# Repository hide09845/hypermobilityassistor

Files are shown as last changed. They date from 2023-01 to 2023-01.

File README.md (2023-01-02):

# The HAND
The HAND (A.K.A. the Hypermobility Assistance Device) is a combination wrist and knuckle brace that intends to provide a free, open-source, and 3d-printable alternative to the pricey and/or usually under/overeffective wrist braces on the market.

# What is the HAND made up of?
The HAND is composed of four primary parts- the upper plate, the lower plate, the upper cuff, and the lower cuff. 

![An image of the HAND Four white arrows are pointing towards the upper plate, lower plate, upper cuff, and lower cuff. The upper plate is the largest of the four parts, appearing as a thin piece that spans a little bit over the knuckle, and connects to the upper cuff via a screw located on the wrist joint, allowing it to rotate in tandem with the wrist. The upper cuff is a semicylinder, with two rectangular "wings" that allow it to connect to the upper plate. The lower cuff is identical to the upper cuff, but with a circle taken out of the area near the wrist joint to allow it to move. The lower cuff is attached to the upper cuff via six rubber bands, with only 3 visible in the image. The lower plate is not directly touching the upper plate, but is connected with four elastic cords, the ends of which have cord stops to allow for adjustable tightness.](https://mayamainvert.neocities.org/hand2.jpg)

They will be referred to as such for the remainder of this document.

# What does it excel at?
The HAND mechanically limits the rotation of your wrist vertically and horizontally, meaning your wrist's mobility will approximately match that of the average person. This is built for fine motor activities such as writing or drawing, as well as any activity that requires a large amount of wrist movement. This offloads much of the muscular usage required to keep your joints from overextending to the device, reducing the pain and fatigue caused by repetitive activities. 

The HAND **will** help reduce pain from typing. However, it limits horizontal movement of the wrist to the wiggle room of the device (and the lower plate may interact with the keyboard unless you are typing with your hands raised), which can make typing awkward in some positions.

# Warnings
Do not eat while wearing the HAND. Like most other 3d-printed goods, pieces of food and dirt can get stuck in the grooves of the print. The HAND may alleviate pain while eating with silverware, but it will pose an actual danger to your health. 

Do not lick the HAND or place your mouth on it. Again, dirt and bacteria WILL get stuck in the grooves of the print, and you WILL be at risk of illness.

# How to scale the HAND in your software
Note: The upper plate, upper cuff, and lower cuff MUST be scaled with each other without any stretching. The lower plate can be whatever size fits your palm, as long as the cord/string/wire you use to connect it to the upper plate fits both sets of holes. 

What you need (aside from the main pieces)

- Two screws and two nuts, the size is determined by how much/whether you scaled the device. Measure the hole attached to the wings of the upper cuff to figure out the screw and nut size.
- A sheet of padding of a thickness that you decide
- Cord/string/wire of your choice, preferably elastic, and four cord stops for adjustability
- Six rubber bands of a reasonable size (they can be double wrapped to shorten them)

Measure your hand from the base of the metacarpus to the edge of your knuckle, then scale the upper plate such that the place that the plate cuts off (not including the "wings" of the plate) extends about 1.5 to 2.5cm past your knuckle. 

this

Don't worry too much, as long as it braces your knuckle joint. If it's correctly calibrated, your knuckle shouldn't be able to hyperextend more than 15+-5 degrees without extensive effort.

Place the wings of the upper plate through the wings of the upper cuff so the holes match, then slot the two screws in outwards (such that if you screwed the nuts on, they would face outward). Then, screw the nuts on. 

After this, cut your cord into two long pieces. You can trim it down later, or just leave it long. Slot the cord through the holes in the lower plate (two holes per cord). Pretty much any configuration would work, but I have it slotted through like so:

Image of the lower hand plate, the cord is slotted outwardly on each side

After this, you're going to want to place one end of the cord into each hole of the upper plate, then attach your cord stops.

so2

Then, double wrap the 6 rubber bands and place them onto the little sets of protruding bits on the upper and lower cuff such that it would hold the cuff together. You're gonna want to put your wrist in now to see what thickness of padding you'll need.

Finally, you will want to attach your padding to the upper and lower cuff. You can cut it out and just superglue or hot glue it, but make sure that it fits first by putting it in unadhered, maybe wear it around a bit. If it falls out, it's too loose, if it crushes your wrist/cuts off bloodflow at all you may want to get a different thickness of padding. This is what mine looks like:

This is what mine looks like

# Disclaimers

- The HAND is built for the right hand. You will need to mirror it for usage on the left hand.
- The HAND was designed by a team of two, including myself. I only take partial credit for the design.
- The HAND is a prototype that was designed around my wrist and hand. It may not fit perfectly on all bodies. 
- Do not wear the HAND if you are experiencing any pain as a result of wearing it. 
- If the HAND results in any injury, contact me (mayamainvert@proton.me) so I can place a disclaimer and/or update the STL, or make a pull request. If it cuts the skin, disinfect the wound then file/sand down the area that resulted in a cut. It shouldn't be able to cut you, but some people have more sensitive skin than me and I don't exactly have a broad sample set.
- Contact me (mayamainvert@proton.me) if anything is unclear.

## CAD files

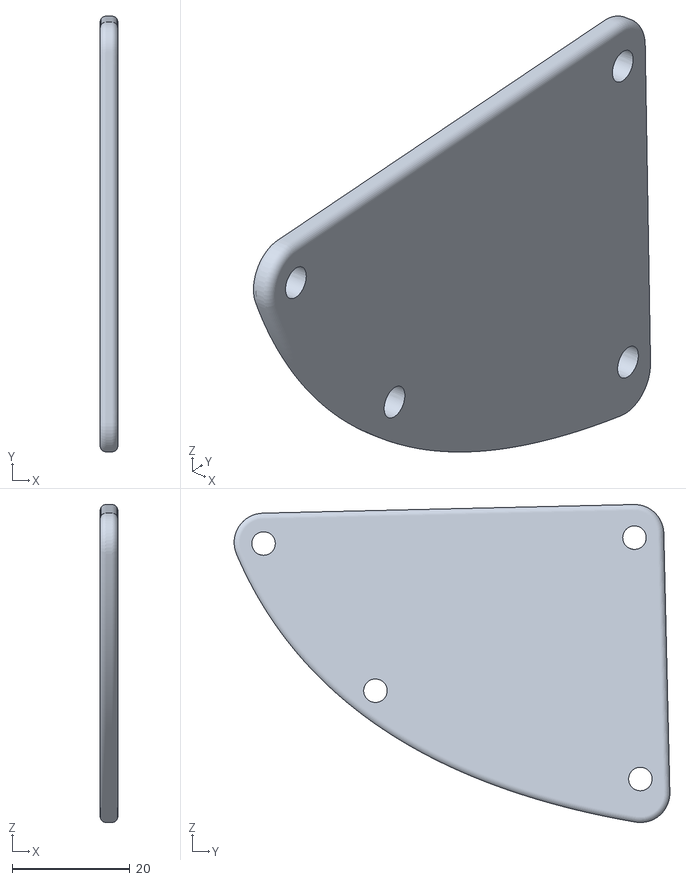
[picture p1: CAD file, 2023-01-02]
lower plate.stl
3.00 x 74.0 x 54.0

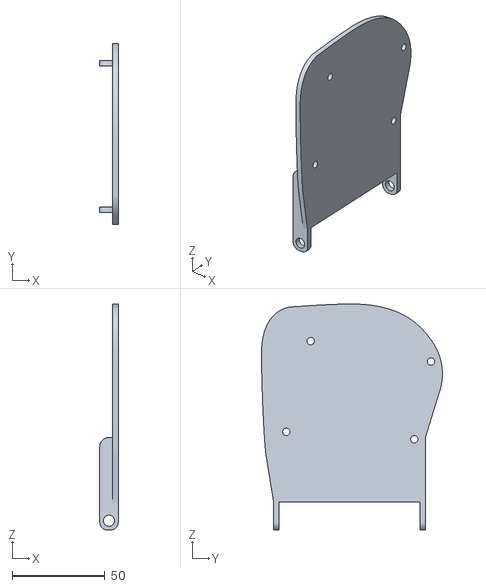
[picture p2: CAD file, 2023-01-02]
upper plate.stl
10.0 x 97.7 x 122.1

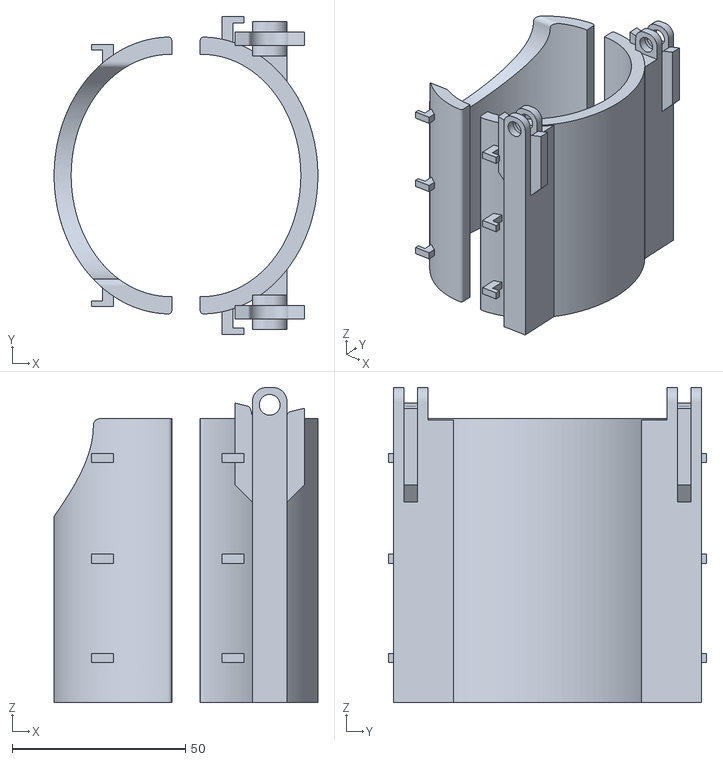
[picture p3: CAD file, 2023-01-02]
upper+lower cuff.stl
76.2 x 92.0 x 91.0
